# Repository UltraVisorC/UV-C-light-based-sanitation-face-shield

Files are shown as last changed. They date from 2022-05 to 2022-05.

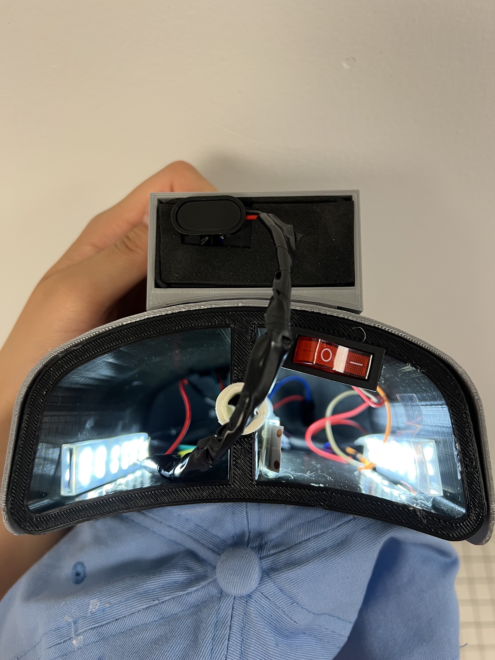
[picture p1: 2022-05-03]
images/Final Fidelity 3.jpg

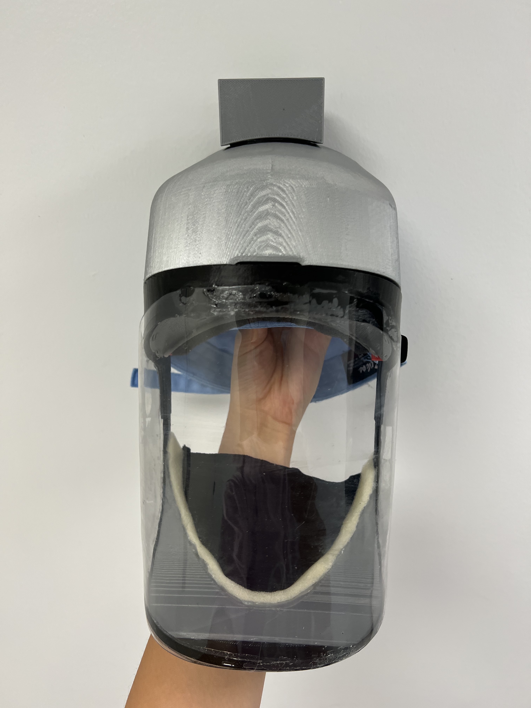
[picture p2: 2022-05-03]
images/Final Fidelity 2.jpg

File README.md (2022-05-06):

# UV-C-light-based-air-sanitation-face-shield

Authors: Sarah Luan, Shifan Liu, Gloria Ni, Christopher Zhou

Team email: ultravisor.c@gmail.com

## The Central Problem 
The current pandemic poses a serious threat to people in high-risk environments, especially doctors and nurses. While there are many protective measures, they are not 100% effective. Our team is tasked with designing a prototype modeled after the UVisor, an existing prototype and face shield that is 99% effective against viruses. The current UVisor is a 2.5 lb faceshield that utilizes UV-C technology to sanitize inhaled air particles and has a battery life of 4-8 hours. Although the UVisor is able to successfully sanitize incoming air, one missing component is its inability to sanitize outgoing air. This poses a safety concern for medical professionals who wish not to infect patients and other staff by viral transmission from exhaled air. 

## Problem Statement
The UltraVisor-C’s central goal is to improve the UVisor by sanitizing exhaled air while maintaining the same weight, sanitation efficacy, and durability. Additional targets include improving battery life, comfort, audibility, and ease of use.

## Modifying the UVisor 
The current UVisor has two fans that blow air downwards in front of the user's face. These fans direct air through the UV-C chamber where the air is sanitized by the UV-lamps. However, this airflow mechanism directes exhaled air downwards and through a hole at the bottom of the device, which is why exhaled air is not cleaned. 

One main modification that we made to the original UVisor to address this issue was separating the UV-C chamber to distinguish inhaled and exhaled air. To do this, we  modified the original CAD file to create a wall in the middle. Another modification we made to the original Visor design was reversing one fan. The components are assembled such that most of the air is sealed inside the product with the built-in airflow mechanism. As shown in the image below, the green arrows represent the direction of the air flowing inside the UVisor. The air is pulled in through the inhale chamber with a fan blowing the air into the visor. After a complete circulation of air within the device, the exhaled air will be directed outwards into the exhale UV-C chamber with the other reversed fan. In our prototype, we used LED lights to model UV-C light. The last main modification we made was creating a sealed bottom. Our device uses foam lining and stretchy cloth to make sure minimal exhaled air is escaping from the sides. The stretchy cloth is velcroed to the bottom so it can be easily detached for cleaning. Some additional components we added to the device include a battery compartment that sits on top of the head and a detachable visor. 



## The Final Prototype
The UltraVisor-C is a face shield. Figure 1 shows the final prototype of our device. The overall product has dimensions of 200mm x 170mm x 290mm, and weight of 916g. The battery holder is situated on top of the sanitation chamber, which is situated on top of the head. The chamber is divided into 2 compartments (one for inhaled air and the other for exhaled), both containing LED strips that act as a substitute for UV-C. Two fans turning in opposite directions direct air between the chamber and the visor. A detachable vinyl visor allows for full face visibility, and the elastic fabric and foam lining prevent air leakage. An adjustable hat helps fix the device on the head. It is detachable and can be replaced to fit the user’s preference.

The prototype used 3D-printed materials for the main structure with Open Source SLDPRT files. These printed parts are attached using epoxy, hot glue, and superglue. For the removable cloth parts, consisting of the hat and the sealing cloth, velcro strips help to attach them to the chamber and visor. Finally, the visor is removable, in case the user needs to eat, drink, or touch their face.



YouTube link of how our prototype works: 
https://youtu.be/ixSwmfPEwCU

## Airflow Testing
Since we did not use real UV-C light, we conducted airflow testing to make sure that air is circulating well throughout the device. To do this, we measured the air being directed into the chamber and the air being directed out the other chamber. Data was collected with an airflow probe, and we placed this airflow probe over the openings of each of the chambers in the back at the same distance. We placed the probe in front of the inhale chamber for about 20 seconds until it had a steady reading, then did the same for the exhale chamber.

We ran 3 trials of this test and our results are shown below in Table 1. Our probe measured the flow rate in and flow rate out in cubed feet per meter. The flow rate in represents the air going into the chamber, while the flow rate out is the flow rate going out the other chamber. We were then able to calculate the volume of air collected in 1 min by making the necessary conversion, which was multiplying the flow rate by about 28. The target value we were trying to achieve is a volume of 6 L/min for both the air going in and the air going out, because that it the average volume that an adult breathes in and out in one minute. As you can see from Table 1 below, all 3 of our trials passed this test. 

Table 1

## Audibility Testing
We conducted audibility testing to measure how much the device affects audibility. For our testing procedure, we first recorded ourselves saying “UltraVisor-C” using voice memos. We played the recording and measured the decibel level it reached using an online decibel meter. Then, we measured the decibel level while a team member wore the device and played the voice memo from inside the visor. Since N95 masks have been proven to reduce speech audibility by about 2.7 decibels, the target value of reduction for each recording is ≤ 2.7 decibels. We conducted 3 trials of this process, and the data is shown below in Table 2. We calculated the average of all 3 trials and then calculated the difference. There was only a 1.867 dB reduction between wearing the device versus speaking normally, so our prototype passed this test. 

Table 2

## Comfortability Testing
In our Comfortability test, we asked 22 people of varying head sizes to wear the device and rate their opinions on a user defined scale, and we then calculated the average of all the ratings according to our User Defined Scale (Table 3). The target value was an average rating of ≥ 4, which specified that the device is easier to breathe in than an N95 mask and components do not get in the way of work. Our final average rating was 3.7, so the device failed the test, and we cannot conclude that the device is comfortable to wear.

Table 3

## Safety and Battery Life
In our Safety test, we first rubbed a balloon across the device surface to ensure that there were no sharp corners, and it did not pop. Secondly, we observed whether electrical wires are exposed on the exterior, and they are not. Thirdly, we ensured that the battery is fully covered and not potentially exposed to sunlight. We repeated the test twice to account for regions that may have been missed by the balloon or battery areas and wires that may have been missed. The device passed all rounds of testing, so we conclude that our device is safe to use. 

In our Battery Life test, we calculated the battery life from our data, given in terms of voltage, milliamp hours. Since it is a straightforward calculation, we performed this test only once. The target battery life is ≥ 8 hours because we assume hospital staff will have a break every 8 hours. The calculated battery life of our device was 32.5 hours, so our device passed the test, and we can conclude that the battery does not need to be recharged during a single shift.

## Strengths and Limitations
The strengths of our current prototype are that we were able to successfully separate the sanitation of inhaled and exhaled air by dividing the UV-C chamber. In addition to the UV-C lamps on the sides, the added UV-C lamp in the middle provides sufficient sanitation for the air passing through. Furthermore, we created a system using fans to direct the air from the inhale chamber to the exhale chamber. Our airflow testing data shows that the rate of air flowing into the inhale chamber is approximately equal to the rate of air flowing out of the exhale chamber. However, our device has a few limitations. Even though our prototype passed the audibility test we created, the decibel measurements do not account for how muffled speech is. We noticed that when teammates wear the device, their speech is significantly muffled. Secondly, our device has some issues involving adjustability. We used elastic fabric to fit the neck area, but the visor frame around the forehead is not as adjustable. In consequence, individuals with larger or smaller neck sizes may find the device uncomfortable. Lastly, we noticed issues with the battery of the prototype. Although our device is projected to last up to 32.5 hours, we discovered that the voltage drops after long periods of time, so the fan does not consistently move at its maximum speed.

## Future Work
For future teams that plan on continuing this project, we hope that our prototype's current limitations can be addressed. First, to address the issue of muffled speech, a microphone speaker system could possibly be implemented in the device. Second, for issues regarding adjustability, different visor sizes could be made for individuals who have larger or smaller head sizes. Lastly, to address the issue of comfortability and dropping battery voltage, a smaller, rechargeable battery could be used to reduce weight on top of the user's head. 

The modified CAD files we created are added to this post, as well as photos of our prototypes. 

## References
https://www.uvisor.org/

https://doi.org/10.1086/503643

https://www.mdpi.com/1996-1944/13/15/3363/htm

https://doi.org/10.37624/ijert/13.7.2020.1562-1566

https://www.ncbi.nlm.nih.gov/pmc/articles/PMC7882915/

https://www.sciencedirect.com/science/article/pii/S1477893920302301

https://doi.org/10.1063/5.0022968

## Acknowledgements
Client: Dr. Robert Read 

Instructor: Dr. Emin Kececi 

Instructor: Dr. Deirdre Hunter

Design Mentor: Charlie Gorton 

Faculty Mentor: Dr. Bilal Ghosn 

Writing Mentor: Rachel Lee

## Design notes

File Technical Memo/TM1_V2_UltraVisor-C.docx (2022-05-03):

DATE: January 31, 2022

TO: Dr. Emin Kececi

FROM: UltraVisor-C Team

SUBJECT: Clarifying UltraVisor-C Team Goals

Addressing the Problem and the Need for UltraVisor-C

The current pandemic poses a serious threat to people in high-risk environments, especially doctors and nurses. While there are many protective measures, they are not 100% effective. Our team is tasked with designing a prototype modeled after the UVisor, an existing prototype and faceshield that is over 99% effective against viruses. One missing component of the UVisor is its inability to sanitize outgoing air. This poses a safety concern for medical professionals who wish to not infect patients and other staff. Another primary concern is the comfort and adjustability of the UVisor design. If the face shield cannot be adjusted to seal the face entirely, contaminated air may leak inside without being sanitized and infect the individual. One potential feature that could be added to the existing UVisor prototype would be to install a set of tubes to differentiate the air that is flowing in versus the air that is flowing out of the UV chamber. Additionally, instead of just having one UV lamp at the forehead, another could be installed near the chin so that air flowing out can be sanitized. The overall purpose of the UltraVisor-C is to use UV-C technology to clear the air from any Covid-19 viruses for the user.

The original project is fully open sourced. As a result, we can use the CAD model to fully understand the technology and design behind UVisor, and further develop our enhancement of the exhalation filtering/cleaning device. Currently, the most widely used PPE is the N-95 mask. Compared to N95 masks, the UVisor/UltraVisor will allow for full visibility of the user’s face, whereas N95 covers half of the face. Hence, the user’s voice would not be muffled, leading to clearer communication. Moreover, the UVisor/UltraVisor will allow for reusability, in addition to increased comfort and sanitation. Furthermore, the UVisor/UltraVisor will also benefit hospitals more than PAPRs (Powered Air Purifying Respirators) because it is more cost-effective, allows for more efficient communication due to better audibility, require the user to periodically replace filters, and has a lower power requirement. From a business perspective, the parts required for the UVisor/UltraVisor aren’t currently in high demand like the PAPR, which allows for more efficient and cost-effective mass manufacturing of the product.

Beginning the Design Process: Plans for UltraVisor-C Design

In the initial “Clarifying Team Assignment” phase of the Engineering Design Process, our team interviewed the client, Dr. Robert Read, who defined the goals and motivations behind our project. The primary objective is to implement a design that sanitizes exhaled air, and additional aims include comfort, durability, and higher battery life. Constraints include the weight, safety, and high viral transmission prevention of the product. In the next phase, “Understanding Problem/Context,” we will conduct extensive research on similar products and methods like N95 face masks, PAPR, CPAP ventilators, BiPAP ventilators, UV-C based devices, etc. We will additionally familiarize ourselves with manufacturing limitations, safety regulations, potential marketing concerns, and necessary background information regarding the UVisor and virus inactivation technology. Our team intends to meet with potential users, who we identified to be medical professionals like doctors and nurses to ascertain their suggested design priorities and how potential factors may affect their performance and safety. We further plan to convene with Ritesh Gupta and Chris Jones, professionals who worked on UVisor, to discuss their research and issues they encountered in their design process.

UltraVisor-C Team Structure

Client: Dr. Robert Read, read.robert@gmail.com

The budget was not a major concern to Dr. Read, so our estimated budget is $500, the maximum allotted by the OEDK.

Our Technical Memo authoring schedule can be found on Table 2, and an overview of our future team activities can be found on our Asana page (Figure 1) and Instagantt page (Figures 2 and 3). Contact information for our team is located in Table 1.

Table 1. Team Contact Information

Name | Email | Phone
UltraVisor-C Team | ultravisor.c@gmail.com
Chris Zhou | cpz1@rice.edu | 832-708-7168
Gloria Ni | ggn1@rice.edu | 346-971-7843
Sarah Luan | sl163@rice.edu | 214-897-6383
Shifan Liu | sl162@rice.edu | 832-908-9147
Charlie Gorton (DM) | ctg4@rice.edu | 516-732-7507
Rachel Lee (WM) | hl92@rice.edu | 224-769-0315
Bilal Ghosn (FM) | bghosn@rice.edu

Table 2. Technical Memo Authoring Schedule

Technical Memo | Due Date for V1 Draft | Author
#1 | Jan 22 | All members

#2 | Jan 29 | Sarah Luan, Chris Zhou

#3 | Feb 5 | Chris Zhou, Shifan Liu

#4 | Feb 12 | Sarah Luan, Gloria Ni

#5 | Feb 19 | Shifan Liu, Gloria Ni

#6 | Mar 5 | Chris Zhou, Shifan Liu

#7 | Mar 26 | Sarah Luan, Shifan Liu

#8 | Apr 2 | Chris Zhou, Gloria Ni

#9 | Apr 26 | All members

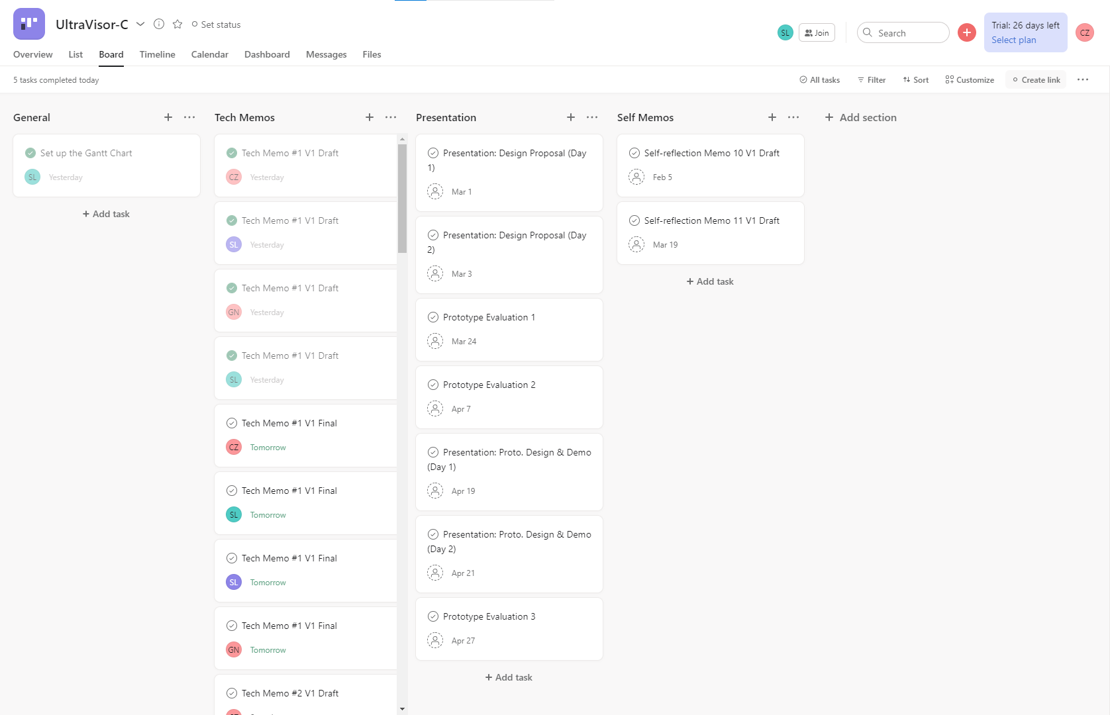
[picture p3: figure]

Figure 1. The UltraVisor-C Team Asana page

The page where team assignments are created. Divided into 4 categories: General, Tech Memos, Presentation, and Self memos.

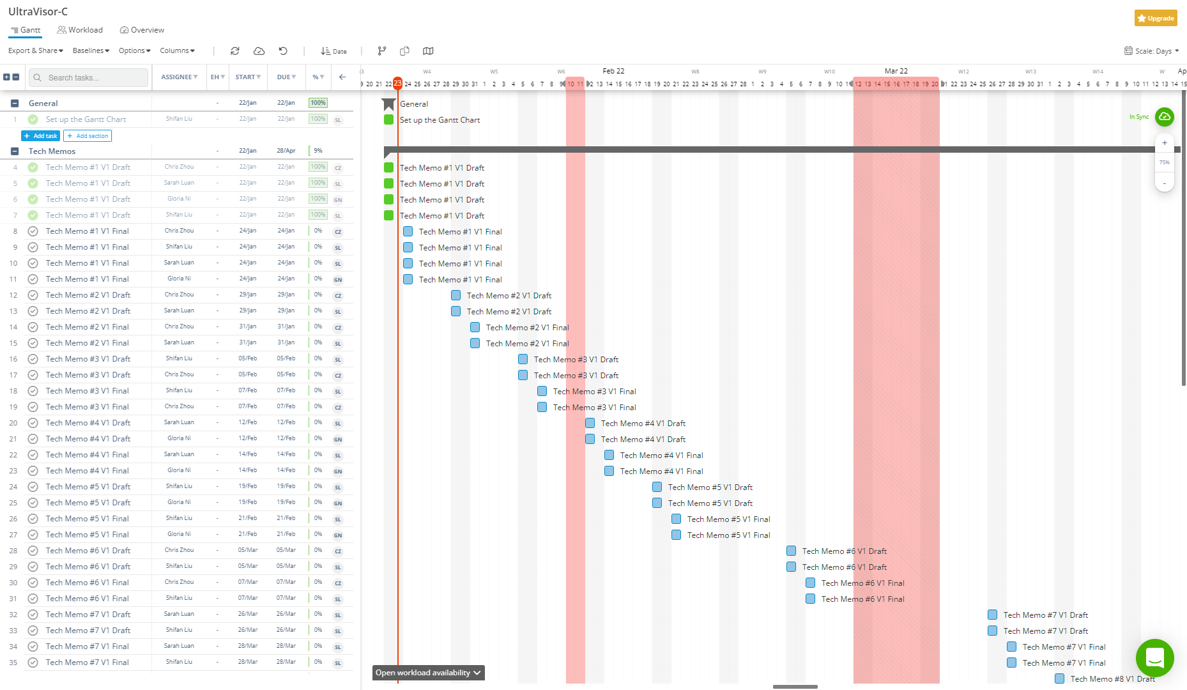
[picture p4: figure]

Figure 2. The UltraVisor-C Team Gantt Chart (Instagantt Page 1)

The Gantt Chart presented in the Instagantt is connected to Asana and shows all the tasks in a clear timeline.

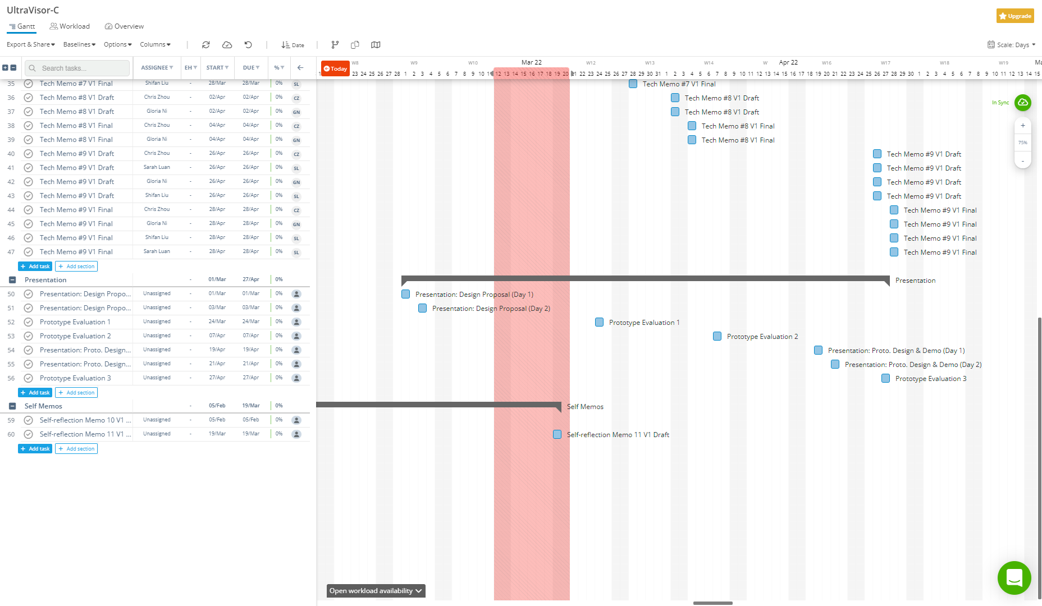
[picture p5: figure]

Figure 3. The UltraVisor-C Team Gantt Chart (Instagantt Page 2)

The Gantt Chart presented in the Instagantt is connected to Asana and shows all the tasks in a clear timeline.

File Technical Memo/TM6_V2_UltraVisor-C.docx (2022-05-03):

DATE: March 5, 2022

TO: Dr. Emin Kececi

FROM: UltraVisor-C Team

SUBJECT: Design Plans for the Prototyping of UltraVisor-C

Engineering Design process Overview of UltraVisor-C

The current pandemic poses a serious threat to people in high-risk environments, especially doctors and nurses. Our team intends to design a prototype modeled after the UltraVisor-C, an existing prototype and faceshield that is over 99% effective against viruses. It uses UV-C light to inactivate the virus thus bringing clean air for users to breathe. However, the missing component of the UltraVisor-C (ability to sanitize outgoing air) poses a safety concern for medical professionals who wish to not infect patients and other staff. The overall purpose of the UltraVisor-C is to improve upon the original UVisor in order to sanitize the exhaled air.

In arriving at our selected solution for the UltraVisor-C, we went through six stages of design. From the problem statement, we first identified what objectives we wanted to achieve (Table 1). Our primary objective was to modify the UltraVisor-C to sanitize exhaled air, with other objectives being to improve the comfort and audibility of the wearer. We then separated these objectives into two categories: structure of the shield and mechanism for regulating airflow. Out of all these categories, we brainstormed a total of 111 partial ideas, which we screened for feasibility to reduce the number to 5 optimal full solutions. Finally, we entered the final complete solutions into a Pugh Scoring Matrix to determine the final solution that best fits our project goals. The original UVisor used two fans to bring air from an inlet, through a chamber (on top of the head) filled with UV-C light, and finally into a visor for users to breathe. The exhalation air would go through the valve at the bottom of the visor without any filtration. Our chosen solution was to modify the original UVisor (Figure 1) by connecting a tube to the exhaust valve at the bottom of the face shield. The tube would connect to the UV-C chamber, which we would divide into two compartments (for inhaled and exhaled air) where the air would be sanitized by the UV-C light and blown out of the chamber by another fan. A sketch of the final solution can be seen in Figures 2 and 3.

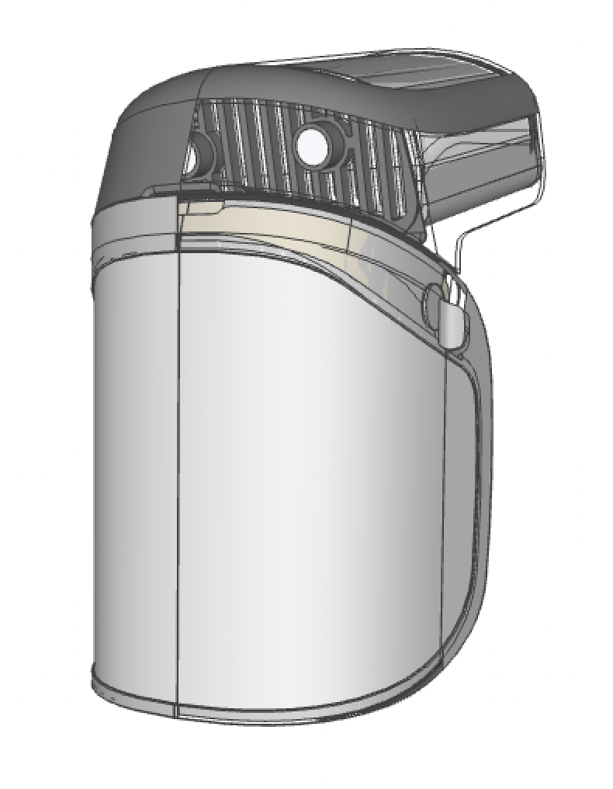
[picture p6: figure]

Figure 1: CAD file of the original solution

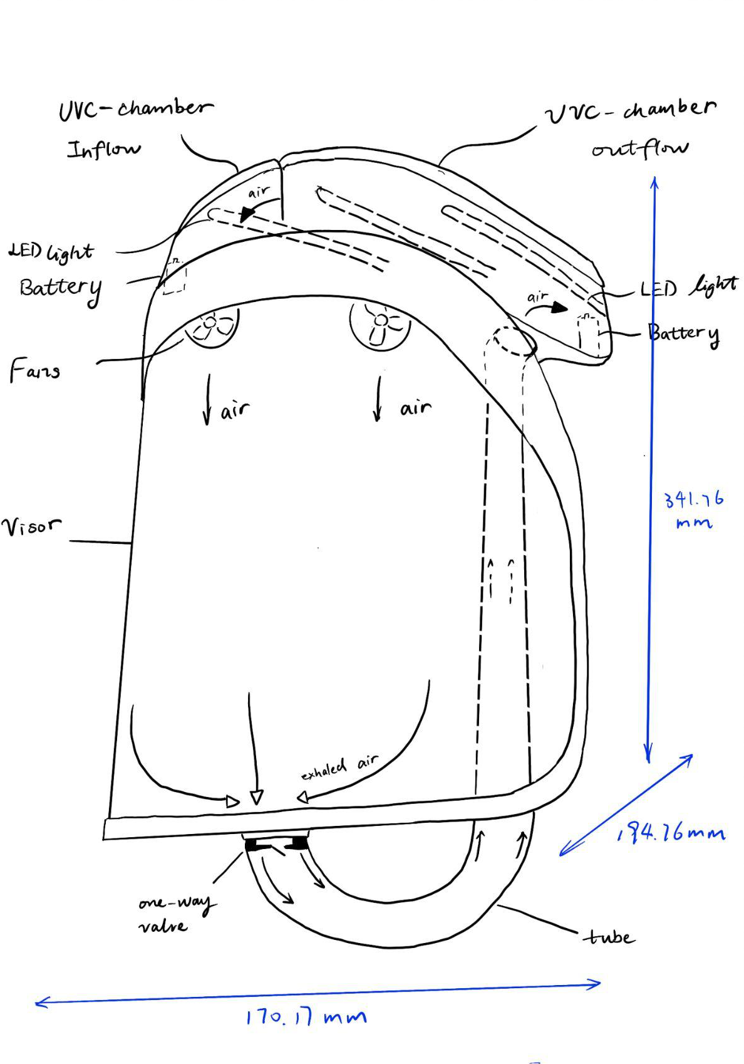
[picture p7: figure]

Figure 2: Sketch of the final solution

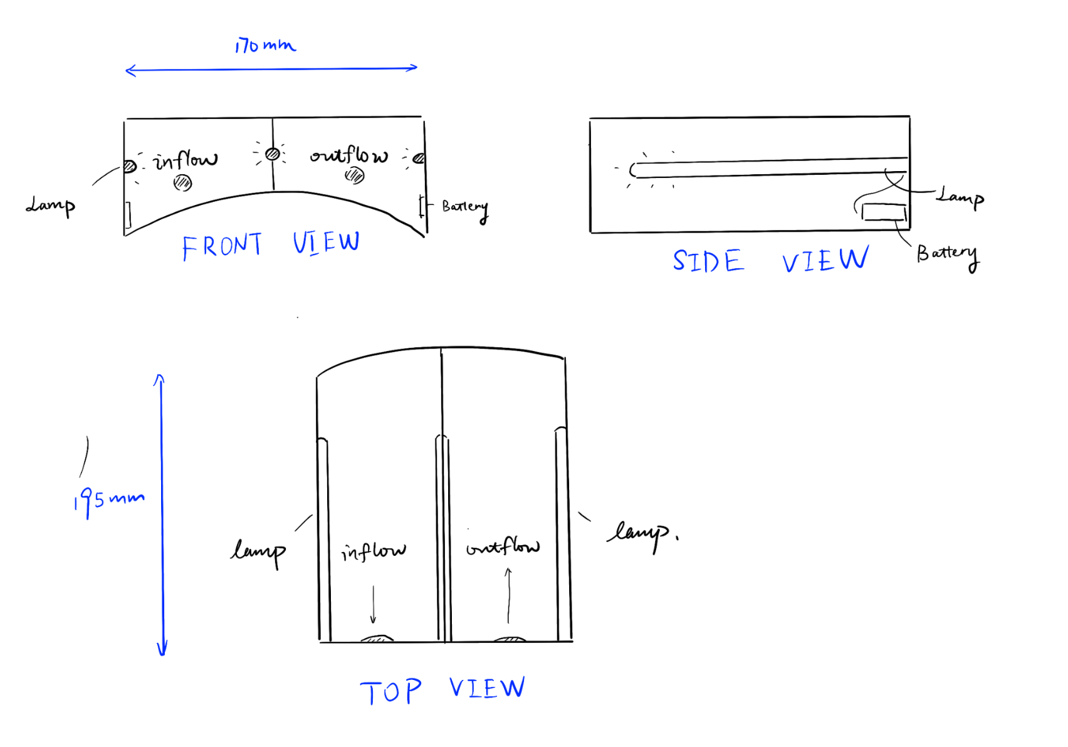
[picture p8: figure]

Figure 3: Sketch of the UVC chamber

Plans for Prototyping the UltraVisor-C

We decided to separate the prototyping of the UltraVisor-C into 3 phases of prototyping: low, medium, and high fidelity prototyping, and two phases of testing: one after the medium fidelity prototype and one after the high fidelity prototype.

Our low fidelity prototype (Figure 4) is a mockup to visualize the structure of the UltraVisor-C, made out of cardboard, tape, hot glue, and a thin plastic tube (Table 1). It is a small scale prototype, as shown in Figure 4, and the completed prototype can be seen in Figure 5. Through this small scale prototype, we are able to see how components should be attached to one another and how our additional modification will fit into the current UVisor design.

The medium fidelity prototype will be a full scale prototype based on Figure 2 and 3. It will have several 3D printed parts, a plastic tube, and working fans, but still use some cardboard components (Table 1). The UV-C chamber and frame of the mask will be 3D printed. However, we will make the divider in the UV-C chamber and the two ports of the tube out of cardboard, as these will need to be adjusted during testing. Furthermore, we will use a sheet of clear plastic for the visor, and a battery to power the fans. We will test this prototype by adjusting both the diameter of the tube and the placement of the divider in the UV-C chamber. This will help us determine what placement of the divider gives us a comfortable airflow for breathing both in and out, while minimizing the diameter of the tube. We will use smoke to visualize the airflow through the mask.

Finally, the high fidelity prototype will be full size and made of all 3D printed parts and have working fans and lamps (used to simulate and test how the UV-C light fills the chamber) (Table 1, Figure 2, Figure 3). We will test this prototype to determine whether the UltraVisor-C successfully achieves our goal of sanitizing the exhaled air. We will once again use smoke to visualize the airflow through the mask.

Table 1: List of component parts

Component | Material
| Low Fidelity | Med Fidelity | High Fidelity
UV-C Chamber | Cardboard | 3D printed plastic (divider and tube connection point made of cardboard) | 3D printed plastic
Face Shield Frame | Cardboard | 3D printed plastic (tube connection point made of cardboard) | 3D printed plastic
Face Shield Visor | None/Paper | Transparent vinyl sheet | Polyethylene terephthalate film
Tube | Plastic | Plastic | Plastic
Fan | Cardboard (only marked position) | 40mm x 40mm x 10mm DC fan | 40mm x 40mm x 10mm DC fan
LED Light Belt | Cardboard (only marked position) | Small LED (Bulbs) | 5.11 inches DC LED Belt
Battery | Cardboard (only marked position) | 9V Battery | 500mA Lithium Battery
One-way Valve | Hole cut by scissors | 0.59 inches (Diameter) valve | 0.59 inches (Diameter) valve

Reflections and Takeaways From Prototyping Design Plan for UltraVisor-C

Our solution had several key features that determined what materials we decided to use in the different prototyping phases. The headpiece to be sturdy because it contains the UV lamps and holds together the rest of the UVisor, so we decided to use cardboard in the low and medium fidelity prototypes for the parts that we were testing and adjusting, and 3D printing in the medium and high fidelity prototypes for the parts that had been tested and finalized. This is because cardboard is sturdy enough to hold its shape, but is still easy to adjust while we are testing, while 3D printed plastic is much more sturdy and durable, but cannot be modified. We decided to leave off the visor in the low fidelity prototype and build the visor frame out of cardboard, since we are mainly testing the structure of the exhaled component. For the medium and high fidelity prototypes, we need to contain the air inside the visor to test airflow and also need something transparent to see if the visor fogs up. For the medium fidelity prototype, we will use transparent vinyl sheets, which are transparent and will hold air, but are cheap at the cost of being flimsy. For this reason, we will use a sturdier PET (polyethylene terephthalate) film for the high fidelity prototype, which is sturdier but more expensive. We decided to use flexible pneumatic tubes for all prototyping phases, since they are cheap and will carry air without leakage.

The biggest technical difficulty of developing our solution will be the addition of the tube and how we will ensure airflow to be directed back upwards through the tube. It’ll be difficult to figure out how thick the tube needs to be to ensure that most of the exhaled air goes through this tube. It’ll also be difficult to model whether or not air is actually going up through this tube and the effect on the inflow air that the user breathes in.

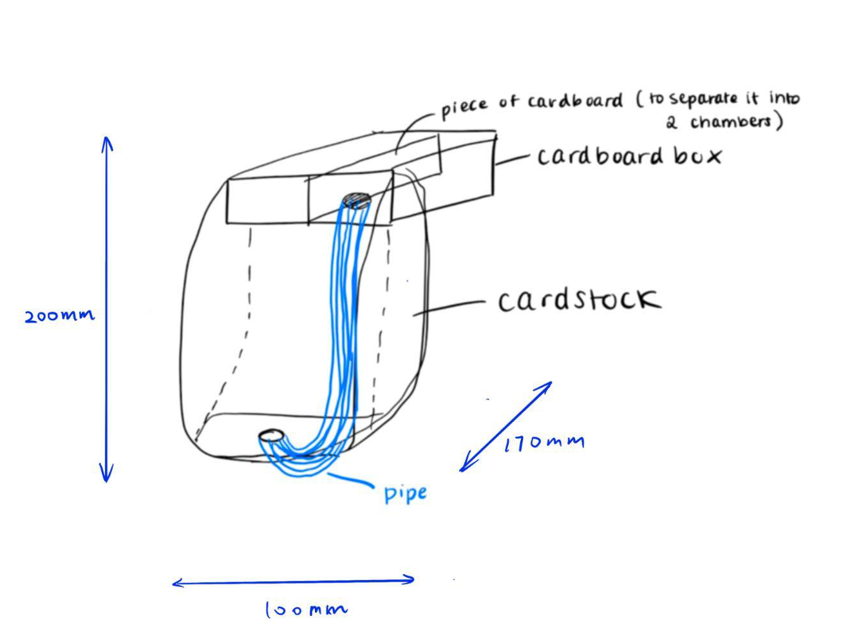
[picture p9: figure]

Figure 4: Sketch of the low-fidelity prototype

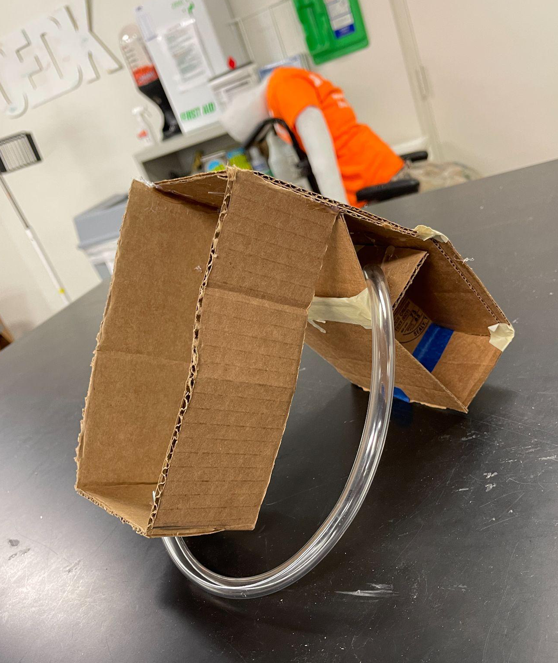
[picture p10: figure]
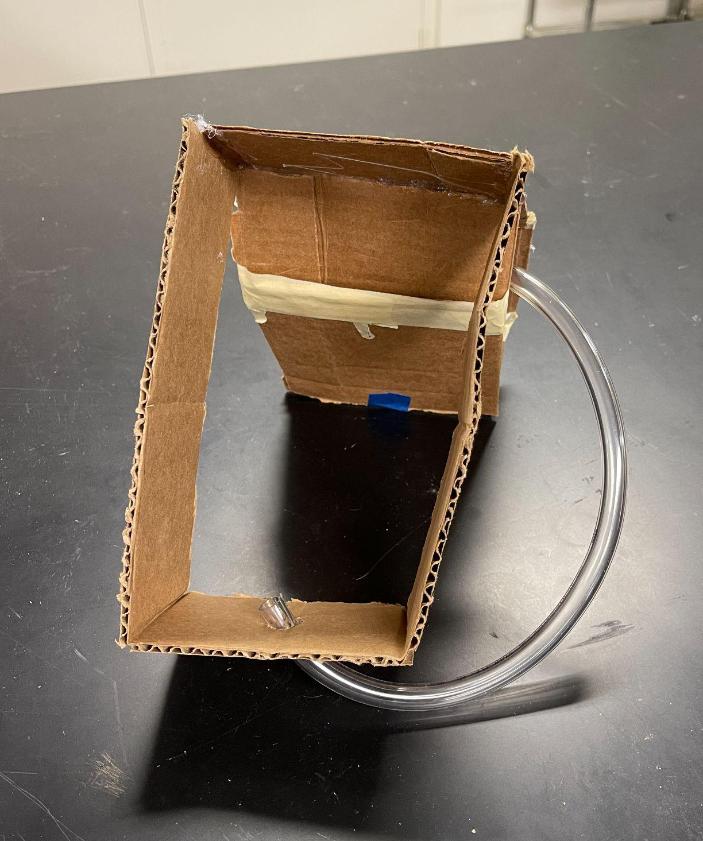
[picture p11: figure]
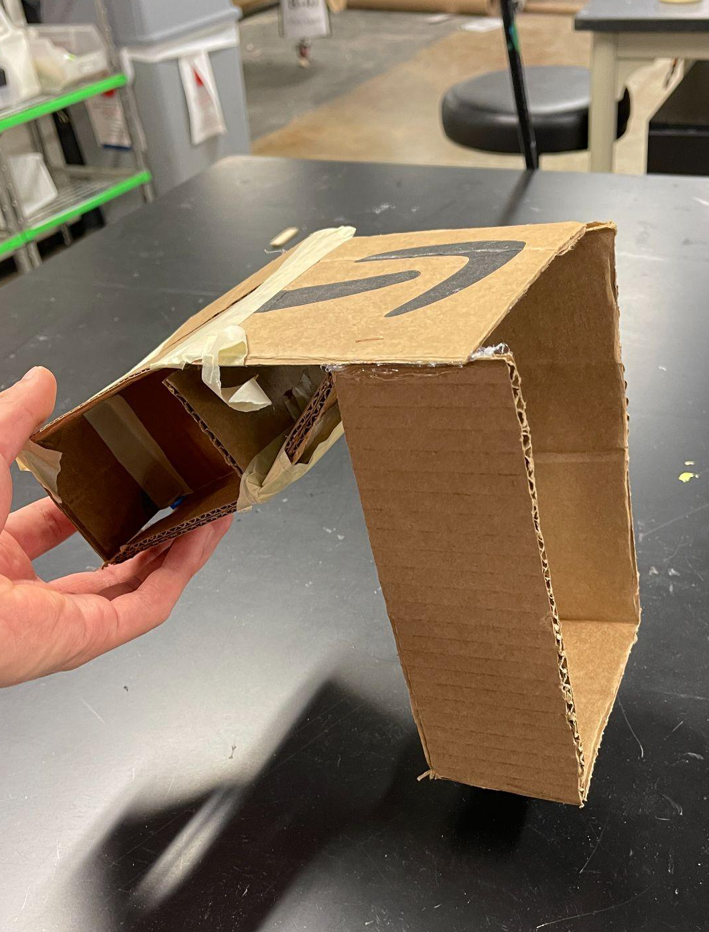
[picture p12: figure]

Figure 5: Low-fidelity prototype (Viewed from Side, Front, Top)

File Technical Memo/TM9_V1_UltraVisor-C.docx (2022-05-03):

DATE: April 27, 2022

TO: Dr. Emin Kececi

FROM: UltraVisor-C Team

SUBJECT: Key Features of the Final UltraVisor-C Prototype

The current pandemic poses a serious threat to people in high-risk environments, especially hospital workers. Our team designed the UltraVisor-C, a device that improves upon the UVisor, an existing face shield that utilizes UV-C technology to sanitize the air. UV-C light has a proven efficacy of 99% against Covid-19. However, a key flaw of the UVisor is its inability to sanitize outgoing air, which poses a major safety concern, since users can infect patients and other staff. The UltraVisor-C builds upon the original UVisor by sanitizing both incoming and outgoing air, in addition to improving the weight, battery life, comfort, audibility, and ease of use.

The UltraVisor-C is a face shield. Figure 1 shows the final prototype of our device. The overall product has dimensions of 200mm x 170mm x 290mm, and weight of 916g. The battery holder is situated on top of the sanitation chamber, which is situated on top of the head. The chamber is divided into 2 compartments (one for inhaled air and the other for exhaled), both containing LED strips that act as a substitute for UV-C. Two fans turning in opposite directions direct air between the chamber and the visor. A detachable vinyl visor allows for full face visibility, and the elastic fabric and foam lining prevent air leakage. An adjustable hat helps fix the device on the head. It is detachable and can be replaced to fit the user’s preference.

The prototype used 3D-printed materials for the main structure with Open Source SLDPRT files. These printed parts are attached using epoxy, hot glue, and superglue. For the removable cloth parts, consisting of the hat and the sealing cloth, velcro strips help to attach them to the chamber and visor. Finally, the visor is removable, in case the user needs to eat, drink, or touch their face.

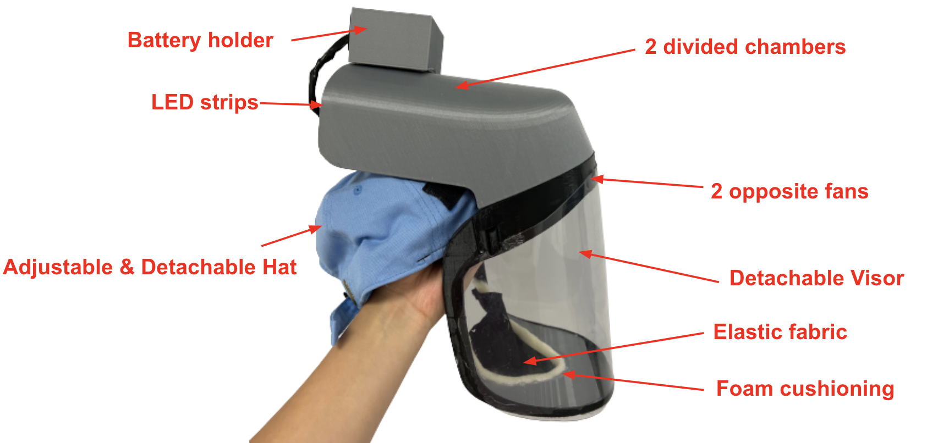
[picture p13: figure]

Figure 1: Final prototype & Components of Ultravisor-C

The components are assembled such that most of the air is sealed inside the product with the built-in airflow mechanism. As shown in Figure 2, the green arrows represent the direction of the air flowing inside the UVisor. The air is pulled in through the inhale chamber with a fan blowing the air into the visor. After a complete circulation of air within the device, the exhaled air will be directed outwards into the exhale UV-C chamber with the other reversed fan.

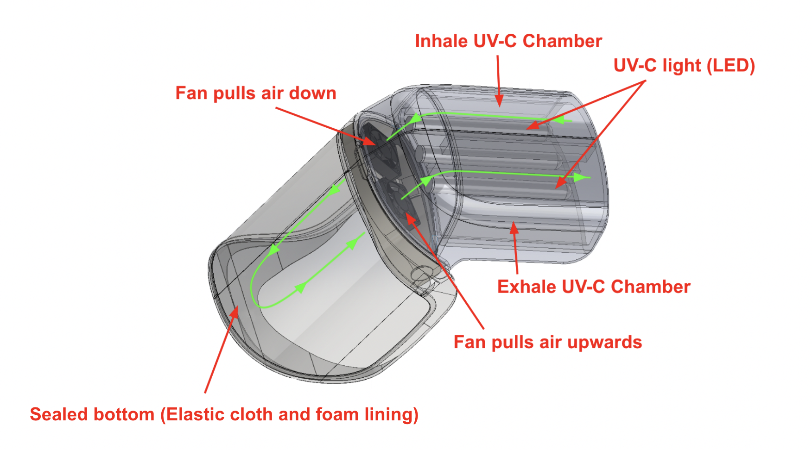
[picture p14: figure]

Figure 2: The airflow mechanism (Circulation of air) of UltraVisor-C

In our Airflow test, we measured the quantity of air entering and exiting the device with an airflow probe. Since we know that UV-C light can achieve an efficacy rate of 99% purification for air entering the UVisor, and we are reusing the same UV-C technology to purify the exhaled air, we know the device achieves 99% purification of exhaled air if airflow entering and exiting the UVisor are equal. First, we placed the airflow probe over opening of the inhale chamber until the reading was steady. We then repeated the process with the probe over the exhale chamber. We conducted 3 trials of this test. The target values for the volume of air entering the device is 10 L/min, the highest volume that an average adult breathes in and out in 1 minute. Since the airflow probe measured in ft³/min, we manually converted the values to L/min to compare with the target value of ≥ 10 L/min. As shown in Table 1, the volume of air entering the device in every trial was ≥ 10 L/min and approximately equal to the volume of air exiting the device, so the device passed the test, and we concluded that the air supply is sufficient and completely sanitized.

Table 1: Flow rate and volume of air in 1 minute

Trial | Flow rate: Air In (cfm) | Volume: Air In (L/min) | Flow rate: Air Out (cfm) | Volume: Air Out (L/min)
1 | 4.6 | 130.257 | 5.2 | 147.247
2 | 5.2 | 147.247 | 5.2 | 147.247
3 | 4.7 | 133.089 | 4.8 | 135.920

We conducted audibility testing to measure how much the device affects audibility. For our testing procedure, we first recorded ourselves saying “UltraVisor-C” using voice memos. We played the recording and measured the decibel level it reached using an online decibel meter. Then, we measured the decibel level while a team member wore the device and played the voice memo from inside the visor. Since N95 masks have been proven to reduce speech audibility by about 2.7 decibels, the target value of reduction for each recording is ≤ 2.7 decibels. We conducted 3 trials of this process, and the data is shown below in Table 2. We calculated the average of all 3 trials and then calculated the difference. There was only a 1.867 dB reduction between wearing the device versus speaking normally, so our prototype passed this test.

Table 2: Decibel measurements of regular speech vs. wearing the device

| Standard (dB) | UltraVisor-C (dB)
Round 1 | 87.1 | 85
Round 2 | 87.4 | 84.8
Round 3 | 86.8 | 85.9
Average | 87.1 | 85.23

In our Safety test, we first rubbed a balloon across the device surface to ensure that there were no sharp corners, and it did not pop. Secondly, we observed whether electrical wires are exposed on the exterior, and they are not. Thirdly, we ensured that the battery is fully covered and not potentially exposed to sunlight. We repeated the test twice to account for regions that may have been missed by the balloon or battery areas and wires that may have been missed. The device passed all rounds of testing, so we conclude that our device is safe to use.

In our Battery Life test, we calculated the battery life from our data, given in terms of voltage, milliamp hours. Since it is a straightforward calculation, we performed this test only once. The target battery life is ≥ 8 hours because we assume hospital staff will have a break every 8 hours. The calculated battery life of our device was 32.5 hours, so our device passed the test, and we can conclude that the battery does not need to be recharged during a single shift.

In our Comfortability test, we asked 22 people of varying head sizes to wear the device and rate their opinions on a user defined scale, and we then calculated the average of all the ratings according to our UDS (Table 3). The target value was an average rating of ≥ 4, which specified that the device is easier to breathe in than an N95 mask and components do not get in the way of work. Our final average rating was 3.7, so the device failed the test, and we cannot conclude that the device is comfortable to wear.

Table 3: User Defined Scale for Comfort

Value | Comfortability
1 | Tubes/battery/other components are extremely inconvenient, prevent movement, and work. Difficult to breathe in.
2 | Tubes/battery/other components are inconvenient and slow down work. More difficult to breathe in than an N95 mask, but still manageable.
3 | Tubes/battery/other components occasionally get in the way of work but it is still manageable to work in. Feels like breathing through an N95 mask.
4 | Tubes/battery/other components don’t get in the way of work but there is a minor impact on performance after prolonged use. Easier to breathe through than an N95 mask, but still feel constrained.
5 | Tubes/battery/other components never get in the way of work and can be worn longer than 4 hours without negative impact on performance. No difficulty breathing.

Although we planned to conduct a Durability test, we have not performed it yet because we need a fully functioning device to present to our client. We planned on conducting a 6 ft drop test on the device to model what might happen if the user were to drop the device from their head. The test will be repeated 3 times because we assume the device would be dropped at most 3 times in the duration of its usage.

The strengths of our current prototype are that we were able to successfully separate the sanitation of inhaled and exhaled air by dividing the UV-C chamber. In addition to the UV-C lamps on the sides, the added UV-C lamp in the middle provides sufficient sanitation for the air passing through. Furthermore, we created a system using fans to direct the air from the inhale chamber to the exhale chamber. Our airflow testing data shows that the rate of air flowing into the inhale chamber is approximately equal to the rate of air flowing out of the exhale chamber. However, our device has a few limitations. Even though our prototype passed the audibility test we created, the decibel measurements do not account for how muffled speech is. We noticed that when teammates wear the device, their speech is significantly muffled. Secondly, our device has some issues involving adjustability. We used elastic fabric to fit the neck area, but the visor frame around the forehead is not as adjustable. In consequence, individuals with larger or smaller neck sizes may find the device uncomfortable. Lastly, we noticed issues with the battery of the prototype. Although our device is projected to last up to 32.5 hours, we discovered that the voltage drops after long periods of time, so the fan does not consistently move at its maximum speed.

Video link: https://youtu.be/ixSwmfPEwCU

(https://youtu.be/ixSwmfPEwCU)

Appendix A. Table Showing Test Results

Criteria | Test | Evaluation
Safety | Balloon test | Pass
| Exposed wires count | Pass
Battery life | ≥ 4 hours | Pass
Sanitation of exhaled air | Volume ≥ 6 L/min | Pass
Audibility | ≤ 2.7 dB difference | Pass
Weight | ≤ 2.5 lbs | Pass
Comfort | ≥ 4 on UDS | Fail
Maintainability | Clean time ≤ 30 min | Pass
Durability | 6 ft. drop test | TBD

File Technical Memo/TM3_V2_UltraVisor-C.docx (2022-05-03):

DATE: February 5, 2022

TO: Dr. Emin Kececi

FROM: UltraVisor-C Team

SUBJECT: Generating and Evaluating Design Criteria for the Improved UVisor

Identifying, Quantifying, and Evaluating Design Criteria for the Improved UVisor

The current pandemic poses a serious threat to people in high-risk environments, especially doctors and nurses. While there exist many protective measures, they are not 100% effective. Our team intends to design a prototype modeled after the UVisor, an existing prototype and faceshield that is over 99% effective against viruses. However, one missing component of the UVisor is its inability to sanitize outgoing air. This poses a safety concern for medical professionals who wish not to infect patients and other staff. The overall purpose of the UltraVisor is to improve upon the original UVisor in order to sanitize the exhaled air.

In the “Define Design Criteria” phase of the engineering design process, we clarified the objectives we wanted our modified UVisor to achieve, as well as the constraints. We first identified and created a list of the features we wanted in the UVisor (Table 1). Then we determined whether each feature was a constraint that must be met, or an objective that we would like to reach. After that, we considered our research to determine the exact quantitative values that needed to be met for each constraint, and the values that we would like to meet for each objective. We also found two of our objectives (Comfort and Audibility) to be difficult to quantify objectively. To quantify these, we created two User Defined Scales for comfort and audibility (Tables 2 and 3). Finally, we created a pairwise comparison chart, or PCC (Table 4), where we compared the importance of durability, weight, maintainability, comfort, and audibility to each other to determine which objectives were the most important to us.

For our constraints, they are divided into 3 essential factors: air sanitation, safety, and battery life. (Table 1) Sanitation includes both inhaled and exhaled air. At present, the original UVisor team has already proved 99.9% sanitation of the incoming air. As a result, our UVisor cannot have a disinfection rate less than 99.9%. Another constraint we identified was the safety of the UVisor. As a product aiming for protection, it should have 0 risk of danger for the user. For an electronic device with a UV-C light chamber, we need to eliminate the possibility of electric shock or leakage of toxic UV-C. Therefore, 0% of UV light can contact the skin, there must be 0 exposed wires, and the battery must comply with 100% of the manufacturer guidelines. Lastly, the UVisor is mainly aiming for hospital staff like doctors and nurses. Therefore, the battery life of our product must last longer than a 4-hour-long shift. We will confirm actual shift data with doctors and nurses in the future.

For our objectives, we decided that the UVisor must last longer than five years with regular use. This number was determined after clarifying it with our client, Dr. Read. There are two main replaceable items: the bulbs, which are best replaced after 2-3 years of 8 hour usage a day on top of the head, and the batteries, which will likely degrade over time. For weight, we wanted our modified UVisor to be less than or equal to 2.5 pounds, since the existing UVisor weighs 2.5 pounds, and if our modified UVisor weighed more than 2.5 pounds, it would not be a strict improvement over the original. We also wanted the UVisor to be easily maintainable, so we want the plastic and cloth materials of the device to be easily disassembled and washed in under 30 minutes once a week. For comfort, we wanted a score on the user defined scale (Table 2) greater than or equal to 4. A score of 4 or higher means that the tubes/battery/other components of the UVisor won’t get in the way of the user’s work, and there is no difficulty breathing through it. We identified our users to be doctors and people in healthcare settings, so it’s important that the UVisor doesn’t interfere with their work. Finally, for Audibility, we wanted a score on the user defined scale (Table 3) greater than or equal to 4. A score of 4 means that all the words of the person wearing the UVisor are understandable without repetition. Existing N95 masks can make it difficult to speak and communicate, so we would like the UVisor to be easier to communicate through.

Finally, for the Pairwise Comparison Chart (PCC), we evaluated the weight of each influencing objectives and ranked them from most important to least important, which is: Sanitation of exhaled air, Audibility, Weight, Comfort, Maintainability, and then Durability. We ranked sanitation of exhaled air as our first priority because that is the main goal we want to accomplish for this project. We ranked audibility as our second priority because communication in the hospital can be crucial. Whether it is talking to patients or performing a surgery, the transmission of voice must be clear either coming in or going out. The third one is weight, since wearing a heavy object on the head for a long period of time would become straining and potentially harmful to the user. The fourth one is comfort. This is considered to be relatively important because the hospital staff will need to wear them for at least 4 hours a day. The last two are maintainability and durability. Since these only affect the UVisor outside of the primary work environment, we decided to prioritize the aspects of the UVisor that affect it while it’s actively being used.

Reflections and Takeaways From Design Criteria Generation for the Improved UVisor

We determined our design criteria by speaking with our client, Dr. Read, who stated that the primary goal would be to sanitize exhaled air, and that our main user base would be doctors and nurses. We decided that for the UVisor to be an improvement on existing N95 masks in healthcare settings, it would need to be comfortable to wear, easy to communicate in, and also more effective in sanitizing both inhaled and exhaled air, while also being as durable, lightweight, and easily maintainable as possible. In our PCC (Table 4), we determined that audibility, comfort, and weight were the most important objectives after sanitation, since healthcare professionals work long shifts, where having a heavy object on the head for extended periods of time would be straining, where clear communication is essential.

The criteria that will likely be the most difficult to design for will be maintainability, since allowing the UVisor to be disassembled while also adding other features makes it much more complex than if we just added other features.

Table 1: Design Criteria

| Design Criteria | Target Value
Constraints | Sanitation of inhaled air | Maintain ≥ 99% sanitation
| Safety | 0% of UV light contacts skin, 0 exposed wires, battery complies with 100% of manufacturer guidelines
| Battery life | Battery lasts longer than ≥ 4 hours
Objectives | Durability | Lasts ≥ 5 years with regular use
| Weight | ≤ 2.5 pounds
| Maintainability | Can be disassembled and cleaned in ≤ 30 minutes, must be cleaned ≤ 1 time/week
| Comfort | ≥ 4 in the user defined scale*
| Audibility | ≥ 4 in the user defined scale**
| Sanitation of exhaled air | ≥ 99% sanitized

*Table 2: User Defined Scale for Comfort

Value | Comfortability
1 | Components are extremely inconvenient, prevent movement, and work. Difficult to breathe in.
2 | Components are inconvenient and slow down work. More difficult to breathe in than an N95 mask, but still manageable.
3 | Components occasionally get in the way of work but it is still manageable to work in. Feels like breathing through an N95 mask.
4 | Components don’t get in the way of work but there is a minor impact on performance after prolonged use. Easier to breathe through than an N95 mask, but still feel constrained.
5 | Components never get in the way of work and can be worn longer than 4 hours without negative impact on performance. No difficulty breathing.

**Table 3: User Defined Scale for Audibility

Value | Audibility
1 | User speech is inaudible.
2 | Users need to repeat themselves every time.
3 | Users need to repeat themselves frequently.
4 | Users need to repeat themselves occasionally.
5 | Users don’t need to repeat themselves.

Table 4: Pairwise Comparison Chart

| Durability | Weight | Maintainability | Comfort | Audibility | Sanitation of exhaled air | Total
Durability | - | 0 | 0 | 0 | 0 | 0 | 0
Weight | 1 | - | 1 | 1 | 0 | 0 | 3
Maintainability | 1 | 0 | - | 0 | 0 | 0 | 1
Comfort | 1 | 0 | 1 | - | 0 | 0 | 2
Audibility | 1 | 1 | 1 | 1 | - | 0 | 4
Sanitation of exhaled air | 1 | 1 | 1 | 1 | 1 | - | 5

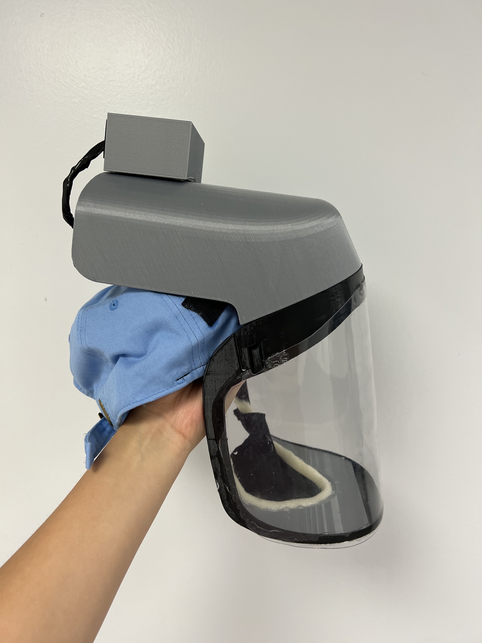
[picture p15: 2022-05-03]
images/Final Fidelity 1.jpg

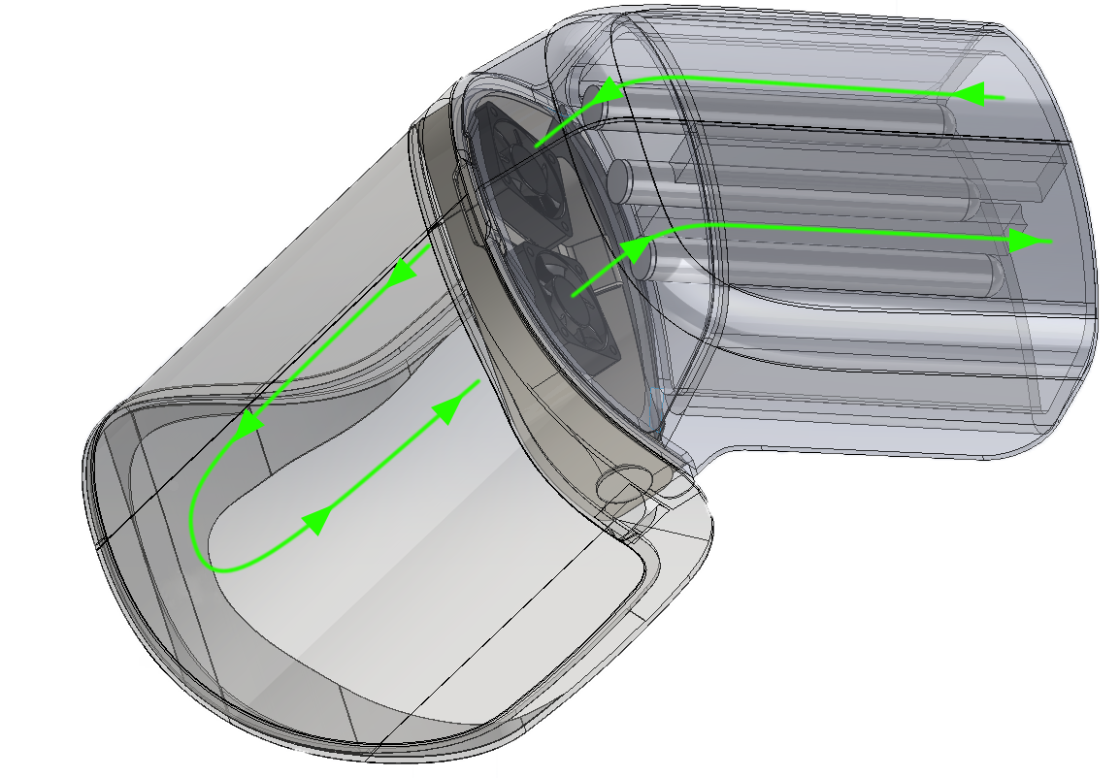
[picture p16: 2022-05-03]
images/UltraVisor-C Airflow Diagram.png

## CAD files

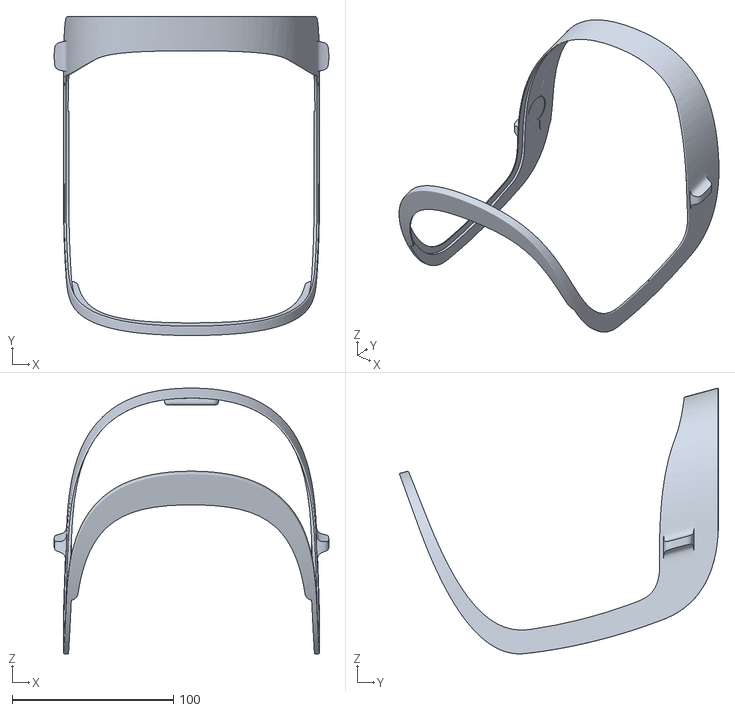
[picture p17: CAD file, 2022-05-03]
CAD Files/Visor_Main.stp-1.STL
170.2 x 197.7 x 164.7

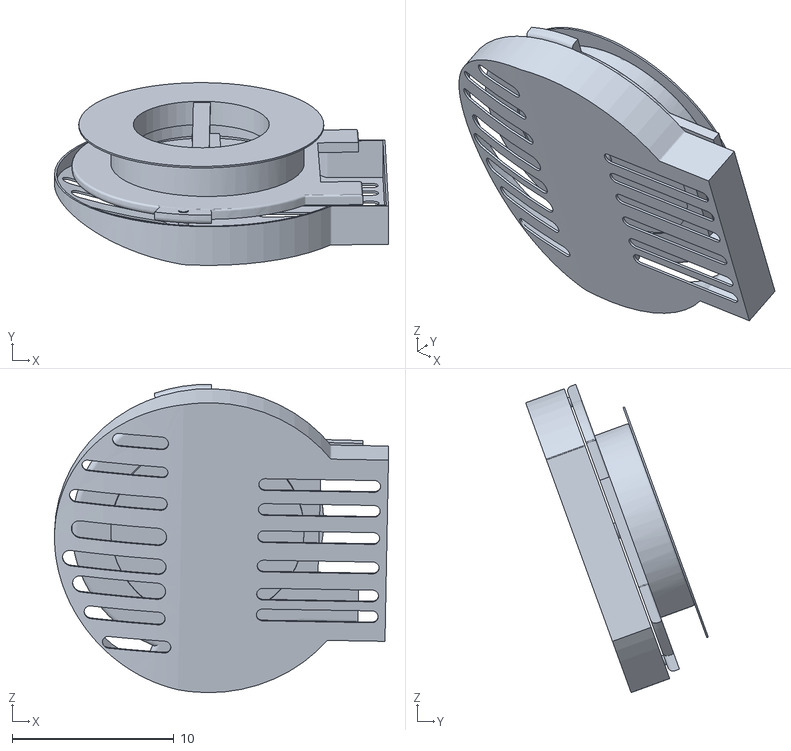
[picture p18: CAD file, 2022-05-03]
CAD Files/Air exchange valve Assembly.stp-1.STL
20.6 x 11.3 x 19.0

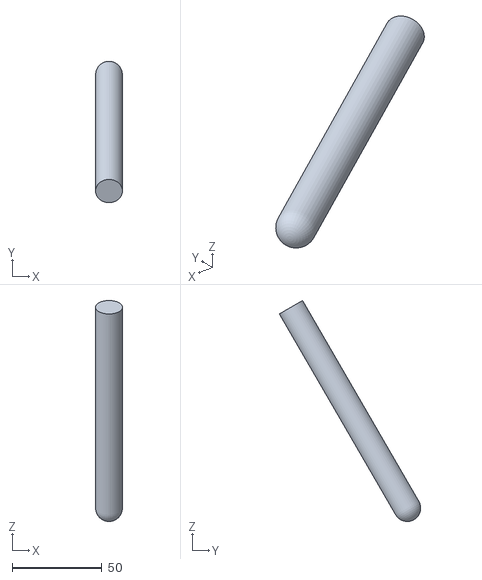
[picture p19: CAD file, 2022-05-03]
CAD Files/Stanley_1W_CompactQuartz.stp-3.STL
15.0 x 78.9 x 123.3

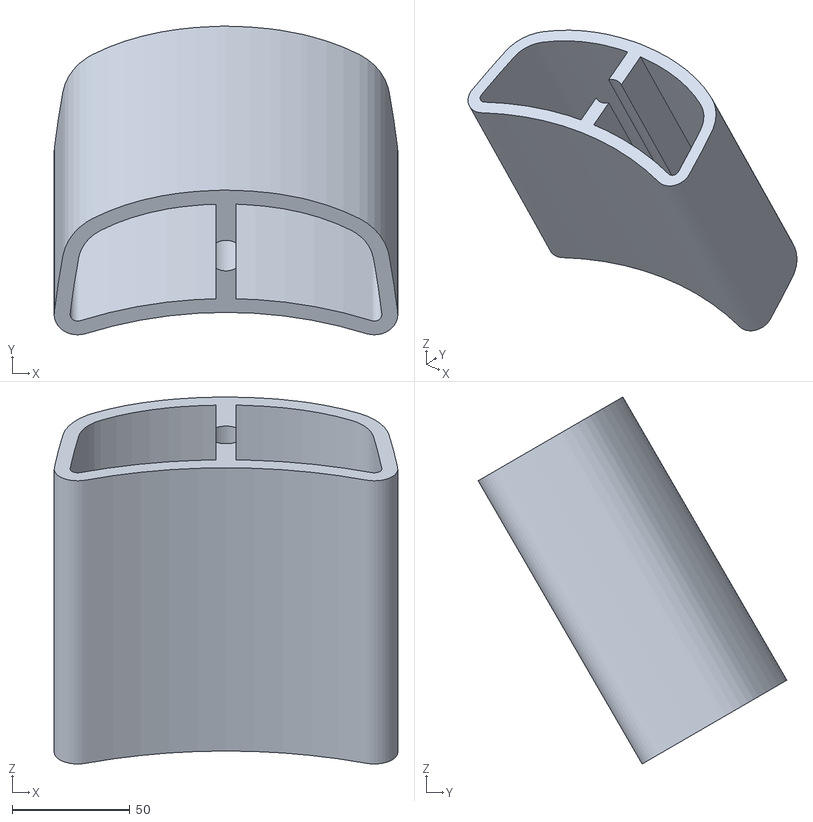
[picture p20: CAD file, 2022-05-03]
CAD Files/BottomConnectedChamber_V1.stp-1.STL
145.9 x 131.1 x 155.9

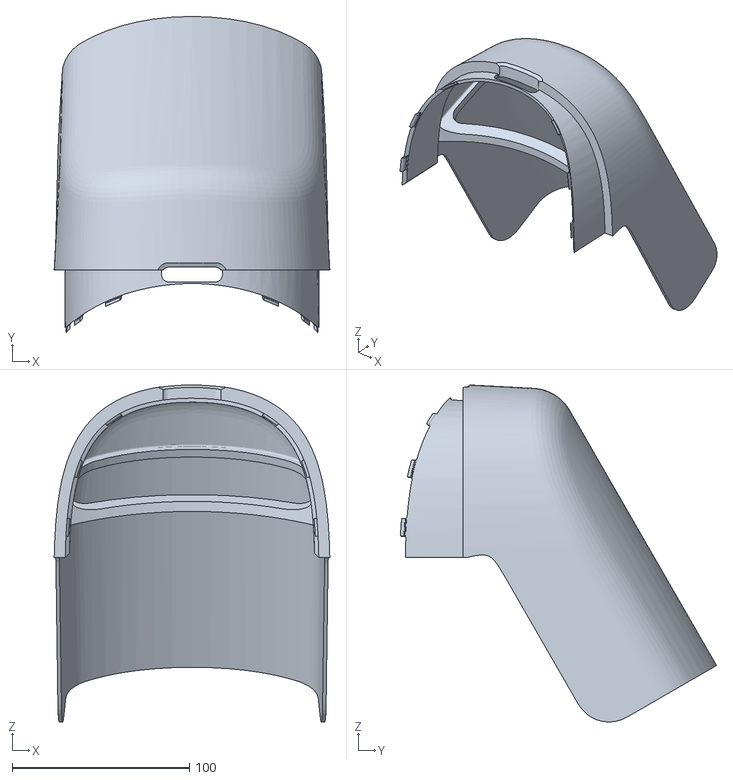
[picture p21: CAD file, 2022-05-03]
CAD Files/A_Cover_2CJV_V2.stp-1.STL
155.6 x 178.4 x 190.2

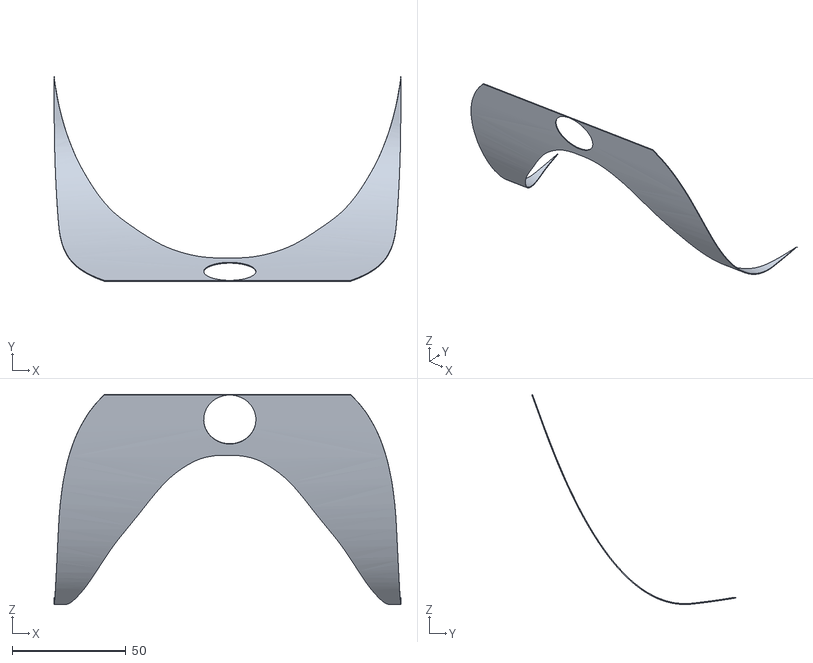
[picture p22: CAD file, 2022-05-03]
CAD Files/Visor_Neoprene.stp-1.STL
152.8 x 90.1 x 92.5

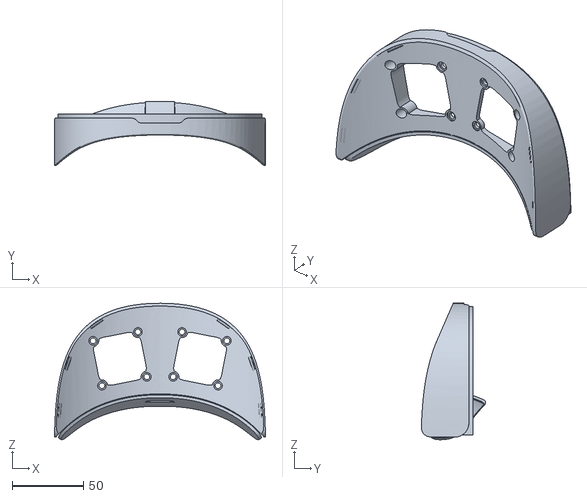
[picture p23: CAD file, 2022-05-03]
CAD Files/Base_Brim_6CJV_2x40mm FAN.stp-1.STL
147.7 x 44.9 x 95.6

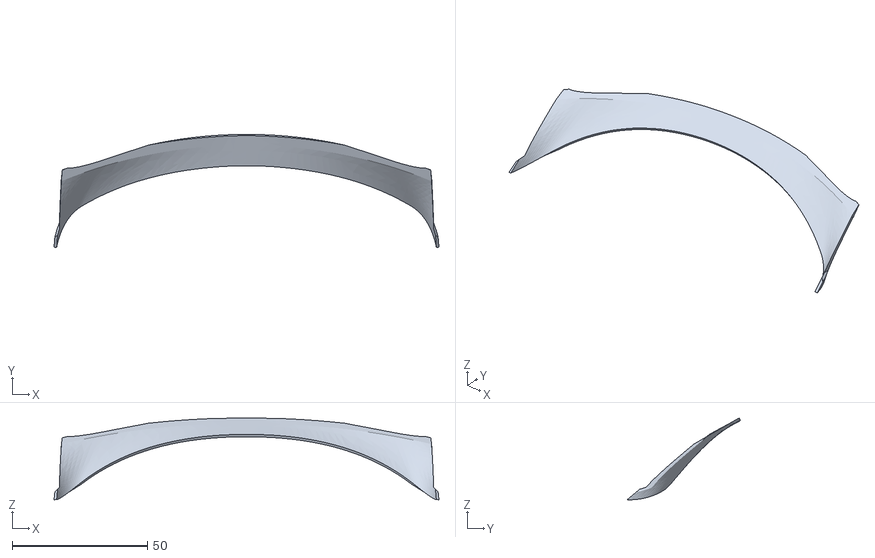
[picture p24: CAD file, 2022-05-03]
CAD Files/ManifoldJoin.stp-1.STL
142.5 x 41.9 x 30.3

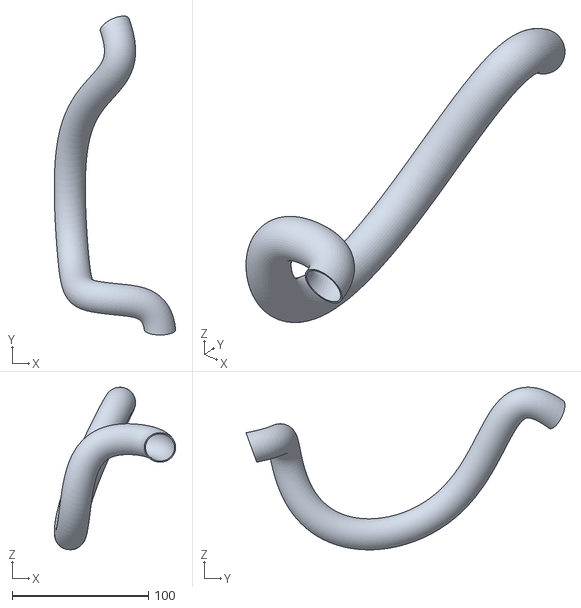
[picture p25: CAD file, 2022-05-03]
CAD Files/Tube V1.stp-1.STL
89.0 x 233.8 x 119.2

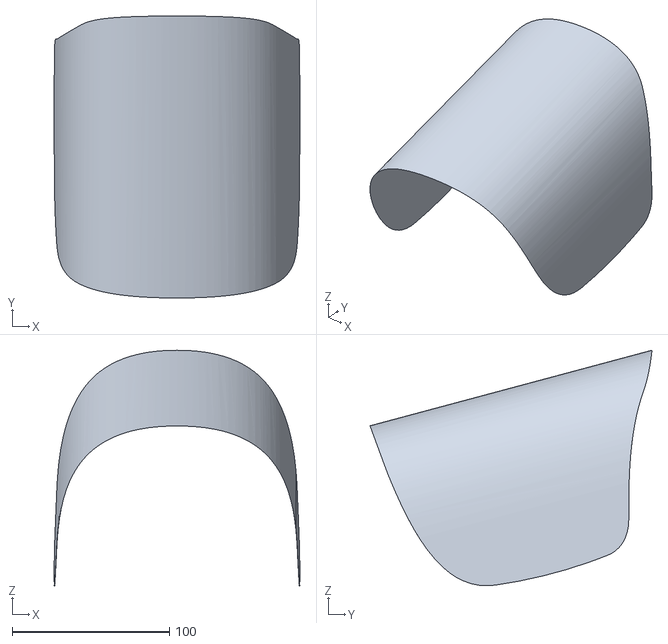
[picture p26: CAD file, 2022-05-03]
CAD Files/Visor_ClearFront.stp-1.STL
156.1 x 179.3 x 149.7

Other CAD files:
CAD Files/Stanley_1W_CompactQuartz.stp-2.STL
CAD Files/Stanley_1W_CompactQuartz.stp-1.STL
